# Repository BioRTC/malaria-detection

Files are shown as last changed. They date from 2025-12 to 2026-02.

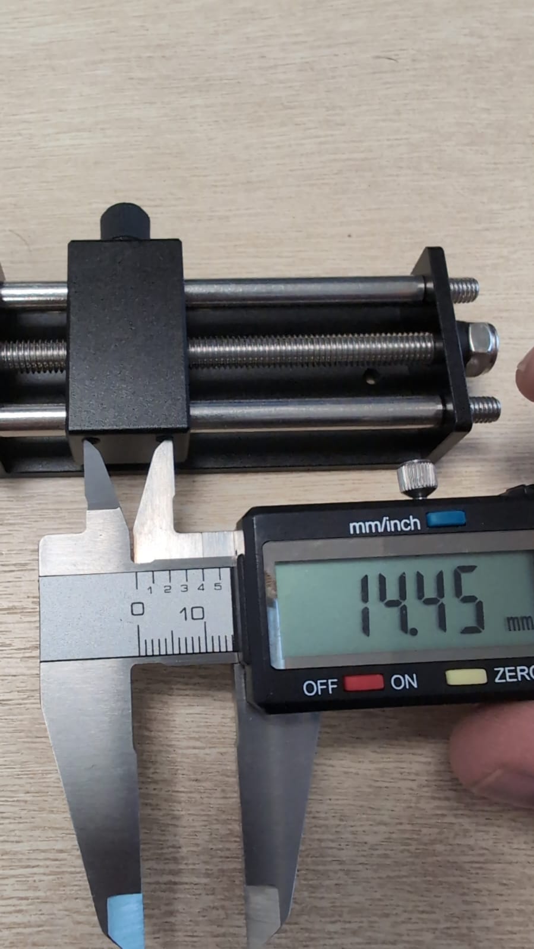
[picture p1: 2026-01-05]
hardware/inverted_YAMM/small_sliding_table/measurements4.jpeg

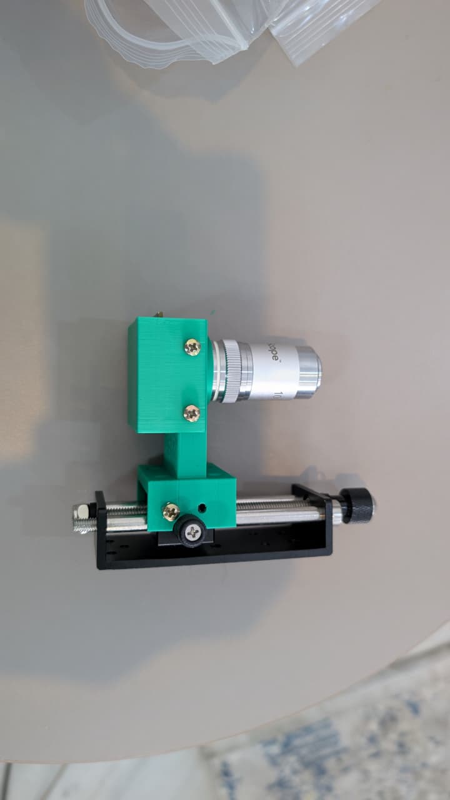
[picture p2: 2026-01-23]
hardware/inverted_YAMM/build_images/optical_mount_n_rail_assembled.jpeg

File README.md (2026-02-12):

# Open source tools and protocols for malaria-detection

This project is developing and deploying a low cost solution for Malaria detecion in [Yobe State](https://en.wikipedia.org/wiki/Yobe_State). Part of the efforts of [BioRTC](https://biortc.com/) and backed by the local government, the goal is to create an open source solution, comprising:  
  
     1- An optical microscope that can digitise data from blood samples and be used in primary health care facilities.  
   
     2- A mechanical machine that allows primary health care workers to make uniform blood smears  
   
     3- standard operating procedures and protocols that show how to collect blood, make the microscope slides, dye them, 
     load slides into microscope and image them, send image to central database.  

# Instructions to build the microscope:

 - https://stepwisedocs.com/docs/projects/yamm-10/guides/microscope-assembly-58#step1

# BOMs:
Find below the bills of materials needed to build the different parts of this project

## Microscope

|quantity|part|detail|cost|link|
|--|--|--|--|--|
|01|manual sliding table|holds printed parts with objective and camera, sets the Z axis positioning|10 USD|[https://aliexpress.com/item/1005006085578165.html](https://aliexpress.com/item/1005008157881482.html)|
|01|Achromatic double lens 50mm focal length|focus image on camera sensor with proper magnification|10 USD|https://aliexpress.com/item/32637177731.html|
|01|achromatic objective 100X oil|using 100X oil so to have the exact same as defined gold standard by world health organisation|25 USD|https://aliexpress.com/item/1005003214487240.html|
|01|immersion oil|objective works with immersion oil|25 USD|https://www.amazon.co.uk/Microscope-Immersion-Olympus-Celestron-20220830/dp/B0BKYPLCDH|
|01| (alternative) immersion oil|objective works with immersion oil|14 USD|https://www.ebay.co.uk/itm/383553538337|
|21|M3X10 Screws|attach parts together|3 USD|https://www.aliexpress.com/item/1005006889828011.html|
|04|M3 nuts|attach parts together|2 USD|https://www.aliexpress.com/item/1005007593861199.html|
|01|8MP USB camera|digitize images|20 USD|https://aliexpress.com/item/1005008613864647.html|
|500g|Black PLA filament|print parts to hold optical assembly and attach it to sliding table|20 USD|https://aliexpress.com/item/1005006809853172.html|
|01|flashlight|illuminate sample - get "tactical flashlight" to change light beam dispersion|20 USD|https://www.aliexpress.com/item/1005006344009961.html|

## materials for sample preparation

|quantity|part|detail|cost|link|
|--|--|--|--|--|
|01|microscope slide|blood is loaded and prepared for microscopy on the slide|5 USD|https://aliexpress.com/item/1005010114618367.html|
|01|blood collection needle|blood from finger is collected for slide preparation|5 USD|https://aliexpress.com/item/1005005066615408.html|
|01|small band aid|cover the puncture made with the needle|5 USD|https://aliexpress.com/item/1005005513455147.html|
|01|gloves|protect health workers from blood contamination|2 USD|https://aliexpress.com/item/1005007990598273.html|
|01|sharp objects waste|collect sharp objects, broken microscope slides, etc|5 USD|https://aliexpress.com/item/1005009050424318.html|
|01|medical waste bag|collect non-sharp medical waste|2 USD|https://aliexpress.com/item/1005008159326306.html|
|01|Pasteur pipette|put a drop of blood on slide|2 USD|[https://aliexpress.com/item/1005008159326306.html](https://www.aliexpress.com/item/1005006549620753.html)|

## materials to dye the blood

TBC

## smear maker

Currently we are replicating the mechanical smear maker described by Mcdermott et al. [here](https://pubs.aip.org/aip/rsi/article/93/1/014104/2848811/autohaem-3D-printed-devices-for-automated)

## file naming convention for images acquired with the microscopes:

- YYYYMMDD_microscopeid_sampleid_ifasmearmakerwasusedornot

so an example would look like with a smear maker would look like:
20251119_m001_s003_maker

and one example without the smear maker would look like:
20251119_m001_s004_manual

||||||
|--|--|--|--|--|
||||||

## literature:

Open source kohler illumination: https://arxiv.org/pdf/1902.10521

## interesting links:

simulation of kohler illumination: https://phydemo.app/ray-optics/gallery/koehler-illumination

## links for future improvements:

- ELP camera: https://grabcad.com/library/usb-camera-module-1
- sliding table: https://aliexpress.com/item/1005008157881482.html
- esp32 controller with camera (choose OV5640 version): https://aliexpress.com/item/1005010184619897.html (UPDATE 18/12/2025 -  this microcontroller 
  does not have enough processing power to transmit 5MP images fast enough for users to be able to focus images. Another shortcoming is that the camera chip
  heats up too much, and it makes the PLA soft)
- grabcad link for the ESP32 controller (to be tested): https://grabcad.com/library/freenove-esp32-s3-wroom-cam-1
- smaller flashlight

## references:

- CAD design for objective in designs comes from Thorlabs https://www.thorlabs.com/item/RMS100X-O

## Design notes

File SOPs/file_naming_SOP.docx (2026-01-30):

## STANDARD OPERATING PROCEDURE (SOP)

### TITLE: Acquiring images,

### 1. PURPOSE

To provide a standardized procedure for saving, naming and sending image information from Malaria testing protocols.

### 2. SCOPE

This SOP applies to all Medical Laboratory Scientists and Technicians involved in acquiring images with YAMM (Yet Another Malaria Microscope) for Malaria detection in the pilot study ran at Damaturu.

### 3. RESPONSIBILITY

- Laboratory Scientists/Technicians: Data aquisition (focused images), naming and transmission.
- Unit Head/Supervisor: Quality control and compliance

### 4. PRINCIPLE

To be able to track the spread of Malaria, its sazonality and its demographics, we need a curated database with collected samples for cross checking and validation.

This will require the following information:

### Collection date

### Location where sample was collected

### Patient Age

### Patient Gender

### pregnancy

### Diagnosis outcome

### If smear maker was used

### And the image itself

### 5. METHOD

### 5.1 Aquiring images at PHCCs

Once diagnosis is made, use the app function to take a photo. Make sure that the system is configured to the highest possible resolution (this should be the default when you open the app). The photo should be saved directly to your phone gallery. Once the photo has been taken, it can be shared with your supervisor via messaging app (whatsapp).

### If you are using whatsapp, make sure to select the “HD” button before sharing. Once the photo has been shared, send a message with information about the photo, in the following format:

### datewithyearfirst_PHCCID_gender_pregnancy_age_microscopediagnosis_rapidtestdiagnosis_smearmakeruse

### One example below, where on Jan 25th 2026 at Gwange PHCC, a test was made with microscopy, using a smear maker, and RDT was also made. Patient was female, 35 years old, pregnant, not smoker

### The filename to be send together with the photo is to your subgroup WhatsApp:

### “20260125_Gwange_F_preg_nonsmoker_45_mpositive_rdtnegative_yesmaker”

### another example below, where on Jan 28th 2026 at Gambir PHCC, a test was made with microscopy, using a smear maker, and RDT was also made. Patient was Male, 55 years old, not pregnant and smoker

### The filename to be send together with the photo is to your subgroup WhatsApp:

### “20260125_Gambir_M_notpreg_smoker_55_mnegative_rdtnegative_yesmaker”

### 5.2 Transferring images aquired to Gdrive

### At this pilot stage we are adding images to a GoogleDrive folder, to serve as an initial database. For this to happen in a useful way the following steps are responsibility of the group leaders:

### - Check the images that were sent on their subgroups and decide if they agree with the microscopy diagnose made.

### - if they AGREE:

### - Upload the image to the shared GoogleDrive folder and rename the image with the name that was sent as text together with the image in the previous step.

### - if they DISAGREE:

### - give feedback on their subgroup about the image, informing why they disagree. In the case the image is inconclusive, ask if it is possible to make new images.

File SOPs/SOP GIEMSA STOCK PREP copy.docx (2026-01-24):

## STANDARD OPERATING PROCEDURE (SOP)

### TITLE:

### Preparation of Giemsa Stock Solution

### 1. PURPOSE

To provide a standardized procedure for the preparation of Giemsa stock solution used for staining blood films for malaria parasites, blood cells, and other hematological or parasitological examinations.

### 2. SCOPE

This SOP applies to all Medical Laboratory Scientists and Technicians involved in blood film staining within the Haematology and Parasitology units.

### 3. RESPONSIBILITY

- Laboratory Scientists/Technicians: Preparation and proper storage
- Unit Head/Supervisor: Quality control and compliance

### 4. PRINCIPLE

Giemsa stain is a Romanowsky stain containing methylene blue, eosin, and azure dyes. It stains nuclei, cytoplasm, and parasites differentially, allowing clear visualization of blood cells and malaria parasites.

### 5. MATERIALS AND REAGENTS

- Giemsa powder (certified)
- Absolute methanol (analytical grade)
- Glycerol (AR grade)
- Measuring cylinder
- Amber-colored reagent bottle
- Glass rod or magnetic stirrer
- Water bath
- Label and marker

### 6. PROCEDURE (STOCK SOLUTION PREPARATION)

1. Weigh 3.8 g of Giemsa powder accurately.
2. Transfer into a clean, dry container.
3. Add 250 mL of glycerol.
4. Warm gently in a water bath at 55–60°C for about 1–2 hours, stirring occasionally until fully dissolved.
5. Remove from heat and allow to cool.
6. Add 250 mL of absolute methanol slowly while mixing.
7. Mix thoroughly to ensure homogeneity.
8. Transfer into an amber reagent bottle.
9. Label with:
  - Name of reagent
  - Date of preparation
  - Expiry date
  - Prepared by

### 7. STORAGE AND STABILITY

- Store at room temperature (20–25°C)
- Keep tightly closed and protected from light
- Allow to mature for at least 1 week before use
- Stable for 6–12 months if properly stored

### 8. QUALITY CONTROL

- Test stain on a known positive malaria blood film
- Ensure:
  - RBCs appear pale pink
  - Nuclei stain purple
  - Malaria parasites stain blue-purple
- Reject stain if precipitate forms or staining quality deteriorates

### 9. SAFETY PRECAUTIONS

- Methanol is toxic and flammable – handle in a well-ventilated area
- Wear gloves and lab coat
- Avoid inhalation and skin contact
- Dispose of waste according to laboratory safety policy

### 10. REFERENCES

1. Cheesbrough M. District Laboratory Practice in Tropical Countries, Part 1
2. WHO. Basic Malaria Microscopy
3. Dacie and Lewis. Practical Haematology

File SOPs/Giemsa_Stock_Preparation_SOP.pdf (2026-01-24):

# Standard Operating Procedure (SOP)

## Preparation of Giemsa Stock Solution

### 1. Purpose

To prepare and use Giemsa stain for microscopic staining of blood films and parasites (e.g., Plasmodium).

### 2. Principle

Giemsa is a Romanowsky-type stain containing Azure, Eosin, and Methylene blue. It differentially stains blood cells and parasites, aiding morphological identification.

### A. Preparation of Giemsa Stock Solution (3.8%)

Reagents:
- Giemsa powder – 3.8 g
- Glycerol (analytical grade) – 250 mL
- Methanol (absolute) – 250 mL
Procedure:
1. Weigh 3.8 g of Giemsa powder.
2. Add it to 250 mL of glycerol in a glass-stoppered bottle.
3. Warm gently in a water bath at 55–60 °C for 1 hour, stirring intermittently until the dye dissolves completely.
4. Add 250 mL of absolute methanol, mix thoroughly.
5. Label as 'Giemsa Stock Solution (3.8%)', including date and preparer’s initials.
6. Store in a dark bottle at room temperature.
7. Allow to mature for at least 1 week before use.

### B. Preparation of Working Giemsa Solution

For thick and thin blood films, dilute 1 part of stock solution with 9 parts of buffered water (pH 7.2). That is, 10% v/v solution — e.g., 10 mL stock + 90 mL buffer.
Buffer Preparation (pH 7.2)
Mix 6.5 mL of KH■PO■ (0.067 M) with 43.5 mL of Na■HPO■ (0.067 M), and make up to 100 mL with distilled water.

### C. Quality Control

- Use known positive and negative control slides.
- Store stain in tightly capped bottles away from sunlight.
- Replace stock if precipitates or color change occurs.

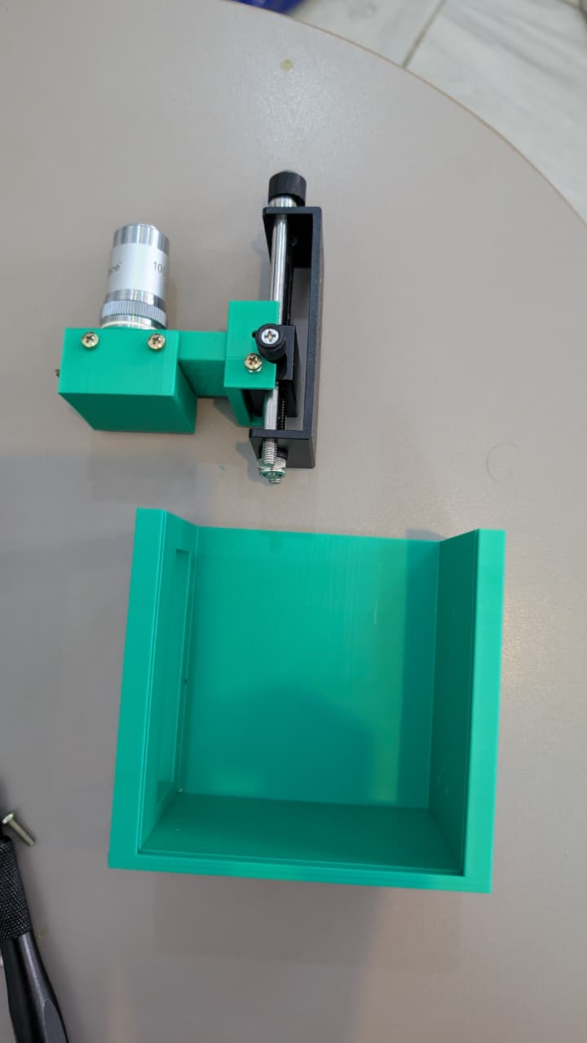
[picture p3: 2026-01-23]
hardware/inverted_YAMM/build_images/optical_n_rail_n_mainbody.jpeg

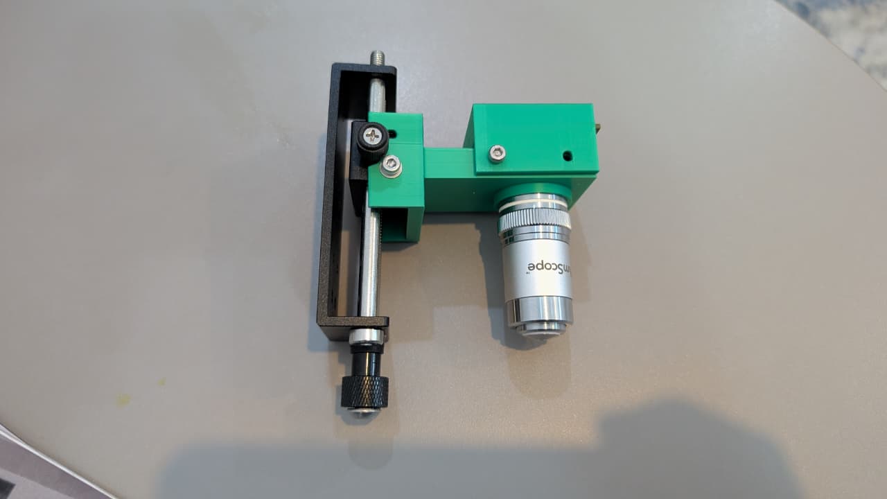
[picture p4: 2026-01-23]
hardware/inverted_YAMM/build_images/rail_n_optics_mounted.jpeg

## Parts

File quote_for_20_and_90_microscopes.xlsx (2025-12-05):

 | item | qty | cost (includes shipping estimate to Nigeria) | total cost | links | obs | 20units | total cost | cost/unit | 90X | total cost | cost/unit
1 | Objective 100X oil | 1 | 32 | 145.35 | https://www.aliexpress.com/item/1005003214487240.html | 100X oil variant | 420 | 2423.39 | 121.1695 | 2072 | 9378 | 104.2 | all prices in USD
3 | OTG cable | 1 | 1.5 |  | https://www.aliexpress.com/item/1005005038133716.html |  | 26 |  |  | 117
4 | Camera | 1 | 21 |  | https://www.aliexpress.com/item/1005008613864647.html |  | 362 |  |  | 1630
5 | Lens | 1 | 14 |  | https://www.aliexpress.com/item/32637177731.html |  | 202 |  |  | 898
6 | PLA Filament for microscope | 1 | 6 |  | https://www.jumia.com.ng/flashforge-pla-3d-printing-filament-high-quality-black-1.75mm-1kg-fdm-3d-printing-material-418826756.html | each spool should make 5 microscopes | 150 |  |  | 540
7 | screws | 1 | 4 |  | https://www.aliexpress.com/item/1005007273134914.html | m3-m5 variant each kit should make 5 microscopes | 80 |  |  | 360
8 | sliding table | 1 | 20 |  | https://www.aliexpress.com/item/1005008157881482.html |  | 450 |  |  | 1800
9 | torch | 1 | 12 |  | https://www.aliexpress.com/item/1005007578277944.html | variant with included batteries & charger | 240 |  |  | 1080
10 | pla filament for smear maker | 1 | 3 |  | https://www.jumia.com.ng/flashforge-pla-3d-printing-filament-high-quality-black-1.75mm-1kg-fdm-3d-printing-material-418826756.html | each spool should make 9 smear makers | 60 |  |  | 270
11 | bushing | 2 | 14 |  | https://www.aliexpress.com/item/1005004320890614.html | m6x8x15 variant | 83 |  |  | 350
12 | metal rod | 1 | 16 |  | https://www.aliexpress.com/item/1005005184865336.html | 6mmX100mm variant | 320 |  |  | 145
13 | magnet | 2 | 1.5 |  | https://www.aliexpress.com/item/1005009819553258.html | 10x3x3mm variant each order makes 5 microscopes | 22 |  |  | 78
14 | nuts | 1 | 0.1 |  | https://www.aliexpress.com/item/1005007593861199.html | m3 variant | 4 |  |  | 18
15 | screws | 1 | 0.25 |  | https://www.aliexpress.com/item/1005007249068859.html | m3x10mm variant | 4.39 |  |  | 20

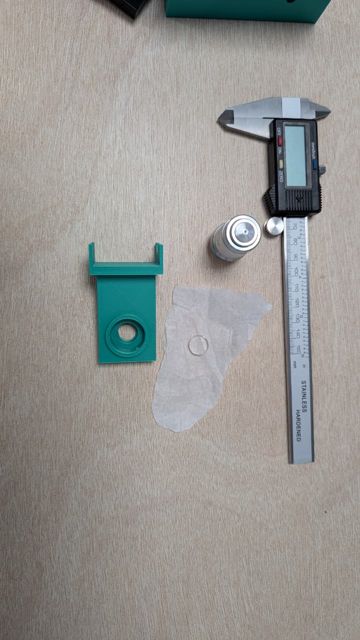
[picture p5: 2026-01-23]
hardware/inverted_YAMM/build_images/optical_components.jpeg

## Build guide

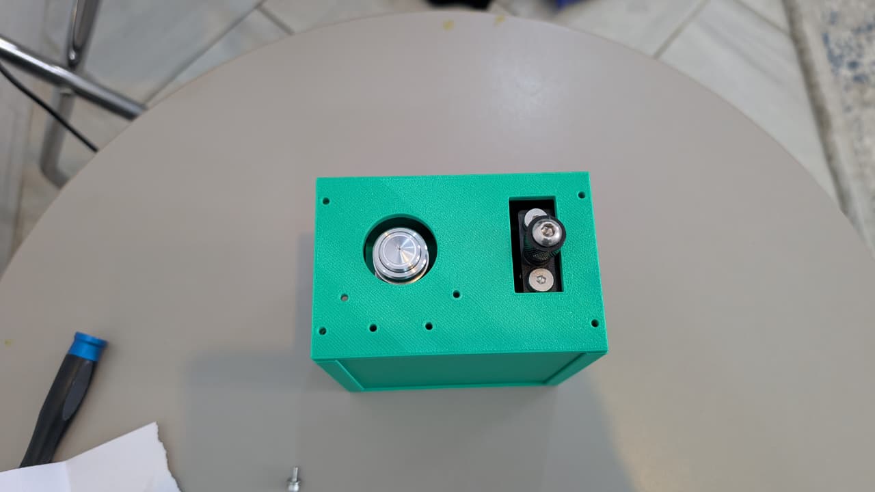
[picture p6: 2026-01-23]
hardware/inverted_YAMM/build_images/top_cover_placement.jpeg

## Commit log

2025-08-21 first attempt to remove mirror
    TRying to remove the mirror in the UC2 scope, so that there is one less point of break/disalisgment, etc...
    the next idea is to put the camera system attached to the objective travel system. then add a tube lens and have in the end a proper microscope
    [XIAO_ESP32S3_Sense_Housing_Design.stl, camera_holder_base.obj, extender.obj]
2025-08-21 update with export files to test
    [camera_holder_base.obj, extender.obj, no_mirror_no_tube_lens.ipt]
2025-08-22 first test with new casing
    [Corpo1.3mf]
2025-10-17 start the port to freecad
    [camera_holder_test.3mf, camera_test.3mf, objective_assembly_test.3mf, objective_holder.FCStd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]
2025-10-17 create v2 of camera holder
    [objective_holder.FCStd]
2025-11-03 organise things and reorient parts in design
    [camera_holder.3mf, camera_holder_test.3mf, camera_test.3mf, objective_assembly_test.3mf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]
2025-11-04 start work on the new system
    [new_system.FCStd]
2025-12-04 add calibration images and quote for ramping up production numbers
    [quote_for_20_and_90_microscopes.xlsx]
2025-12-18 update readme with info on microcontroller and 5MP camera test
2026-01-05 update on microscope design for new sliding table
    [new_system.FCStd, parts_for_seeed_10x_scope.FCStd, test.3mf]
2026-01-05 create files_for printing
    [cover_plate.3mf, main_frame.3mf, objective_holder.3mf, top_plate_frame.3mf]
2026-01-06 created new FreeCad file for small sliding table design
    Since we are not sure all small sliding tables have precisely the same hole arrangement, I have made a new file, so that it corresponds to the small table I have in Brazil. In case the print tests do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
    [scope_with_small_stage_Brazil-camera_holder_v2.3mf, scope_with_small_stage_Brazil-cover_plate.3mf, scope_with_small_stage_Brazil-main_frame.3mf, scope_with_sma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]
2026-01-07 first complete prototype with new sliding table
    [scope_with_small_stage_Brazil-main_frame.3mf, scope_with_small_stage_Brazil-objective_holder_small_table.3mf, scope_with_small_stage_Brazil-top_plate.3mf, scop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]
2026-01-08 create clip holder and light
    backup version of the stage I have in brasil with the correct sample clips and light support
    [parts_for_seeed_10x_scope.FCStd, scope_with_small_stage_Brazil-camera_holder_v2.3mf, scope_with_small_stage_Brazil-camera_holder_v3.3mf, scope_with_small_stage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]
2026-01-23 export correct files for printing
    [camera_holder.3mf, cover_plate.3mf, main_frame.3mf, objective_holder.3mf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]
2026-01-23 fix objective holder dimentsions
    [scope_with_small_stage_Brazil-objective_holder_m3_screws.3mf]
2026-01-23 creating files for printing
    [scope_with_small_stage_Brazil-light_holder.3mf, scope_with_small_stage_Brazil-sample_clips001.3mf, scope_with_small_stage_Brazil-top_plate_with_clip_n_light.3mf]
2026-01-23 change objective holder
    [scope_with_small_stage_Brazil-objective_holder_m3_screws.3mf, scope_with_small_stage_Brazil.FCStd]
2026-01-24 update readme with pasteur pipettes
2026-01-25 add first kohler illuminator draft
    [kohler_illumination_addon-Cut004.3mf, kohler_illumination_addon.FCStd]
2026-01-25 test a new frame design
    [kohler_illumination_addon-Cut004.3mf, kohler_illumination_addon.FCStd, scope_with_small_stage_Brazil-cover_plate.3mf, scope_with_small_stage_Brazil-main_frame.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]
2026-01-27 update sops, scope designand readme
    [Olympus UPlanFL N 20x-0.5.stp, RMS100X-O-Step.step, kohler_illumination_addon-Cut004.3mf, kohler_illumination_addon.3mf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]
2026-02-02 reorganize folders, prepare files for upright microscope version
    [Corpo1.3mf, Olympus UPlanFL N 20x-0.5.stp, RMS100X-O-Step.step, Seeed_Studio_XIAO_ESP32_S3_Sense_3D_Model.step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]
2026-02-12 Fix URL formatting for 8MP USB camera
2026-02-12 update slide rack and prepare things for inverted YAMM
    [inverted_YAMM.FCStd, slide_rack.FCStd]
2026-05-25 remove files that were accidentally added here, but actually belong to a different project
    [COUPLER witt shaft.FCStd, COUPLER.3mf, coupler1.FCStd, shaft.FCStd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]
2026-05-25 prepare print versions of latest design
    [inverted_YAMM-camera_holder_v3.3mf, inverted_YAMM-main_frame.3mf, inverted_YAMM-objective_holder_m3_screws.3mf, inverted_YAMM-side_panel.3mf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]
